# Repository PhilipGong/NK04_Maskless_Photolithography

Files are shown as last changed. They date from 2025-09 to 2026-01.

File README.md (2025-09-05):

# NK04_Maskless_Photolithography
Project repository for developing an LCOS based maskless photolithography process.

---
## Objective
To develope an optical setup which is able to:
- Achieve <= 1um feature size
- Ability to expose photoresists at wavelength (405nm / 465nm)
- (Optional) Step the substrate for wafer stepping
- (Optional) Make use of the phase-shift ability of LCOS for phase shift masking

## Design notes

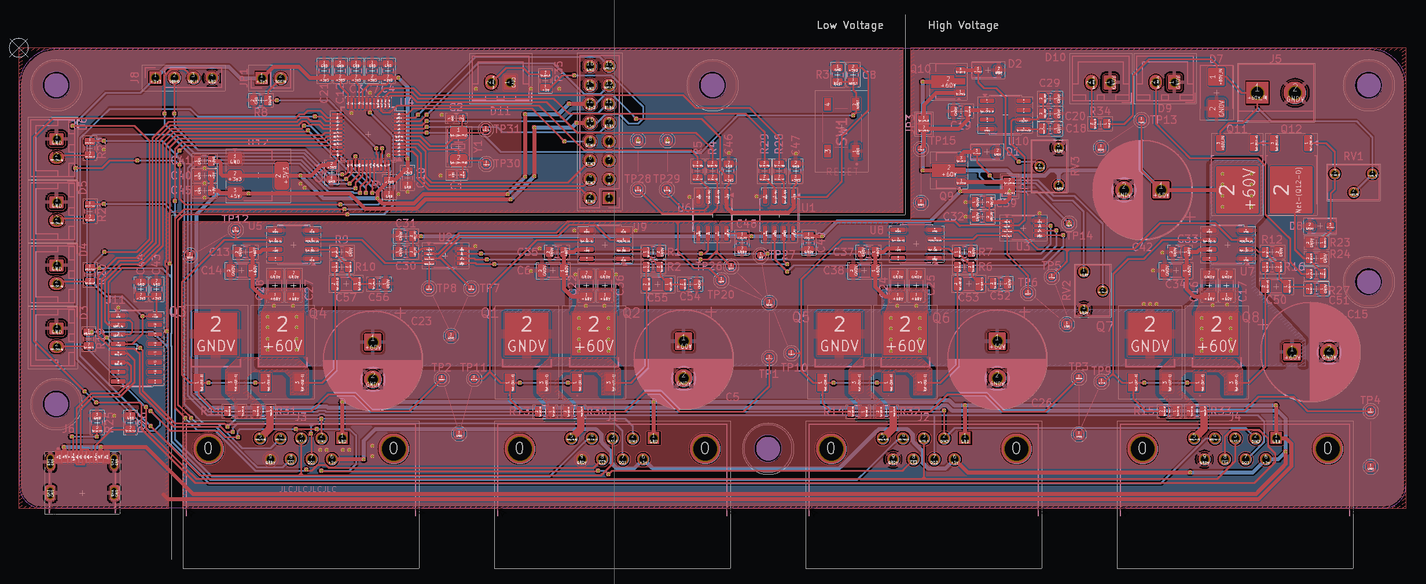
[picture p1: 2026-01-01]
Nanopositioner/Electronics/PCB_Screenshot.png

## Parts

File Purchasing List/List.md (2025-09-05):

## Objective
### Requirements:
- Magnification of 100x
- Numerical aperture of 0.95 or above
- Preferrably working in <400nm of light
### Possible candidates:
- TBD

---

## Photoresist
### Requirements:
- Ability to be exposed by 405nm / 435nm (g-line) / 365nm (i-line) of light
### Possible candidates:
- AZ703

---

## Movement stage
### Requirements:
- 3-axis / 5-axis
- Manual / Motorized (can be developed for autofocusing)
### Possible candidates:

- TBD

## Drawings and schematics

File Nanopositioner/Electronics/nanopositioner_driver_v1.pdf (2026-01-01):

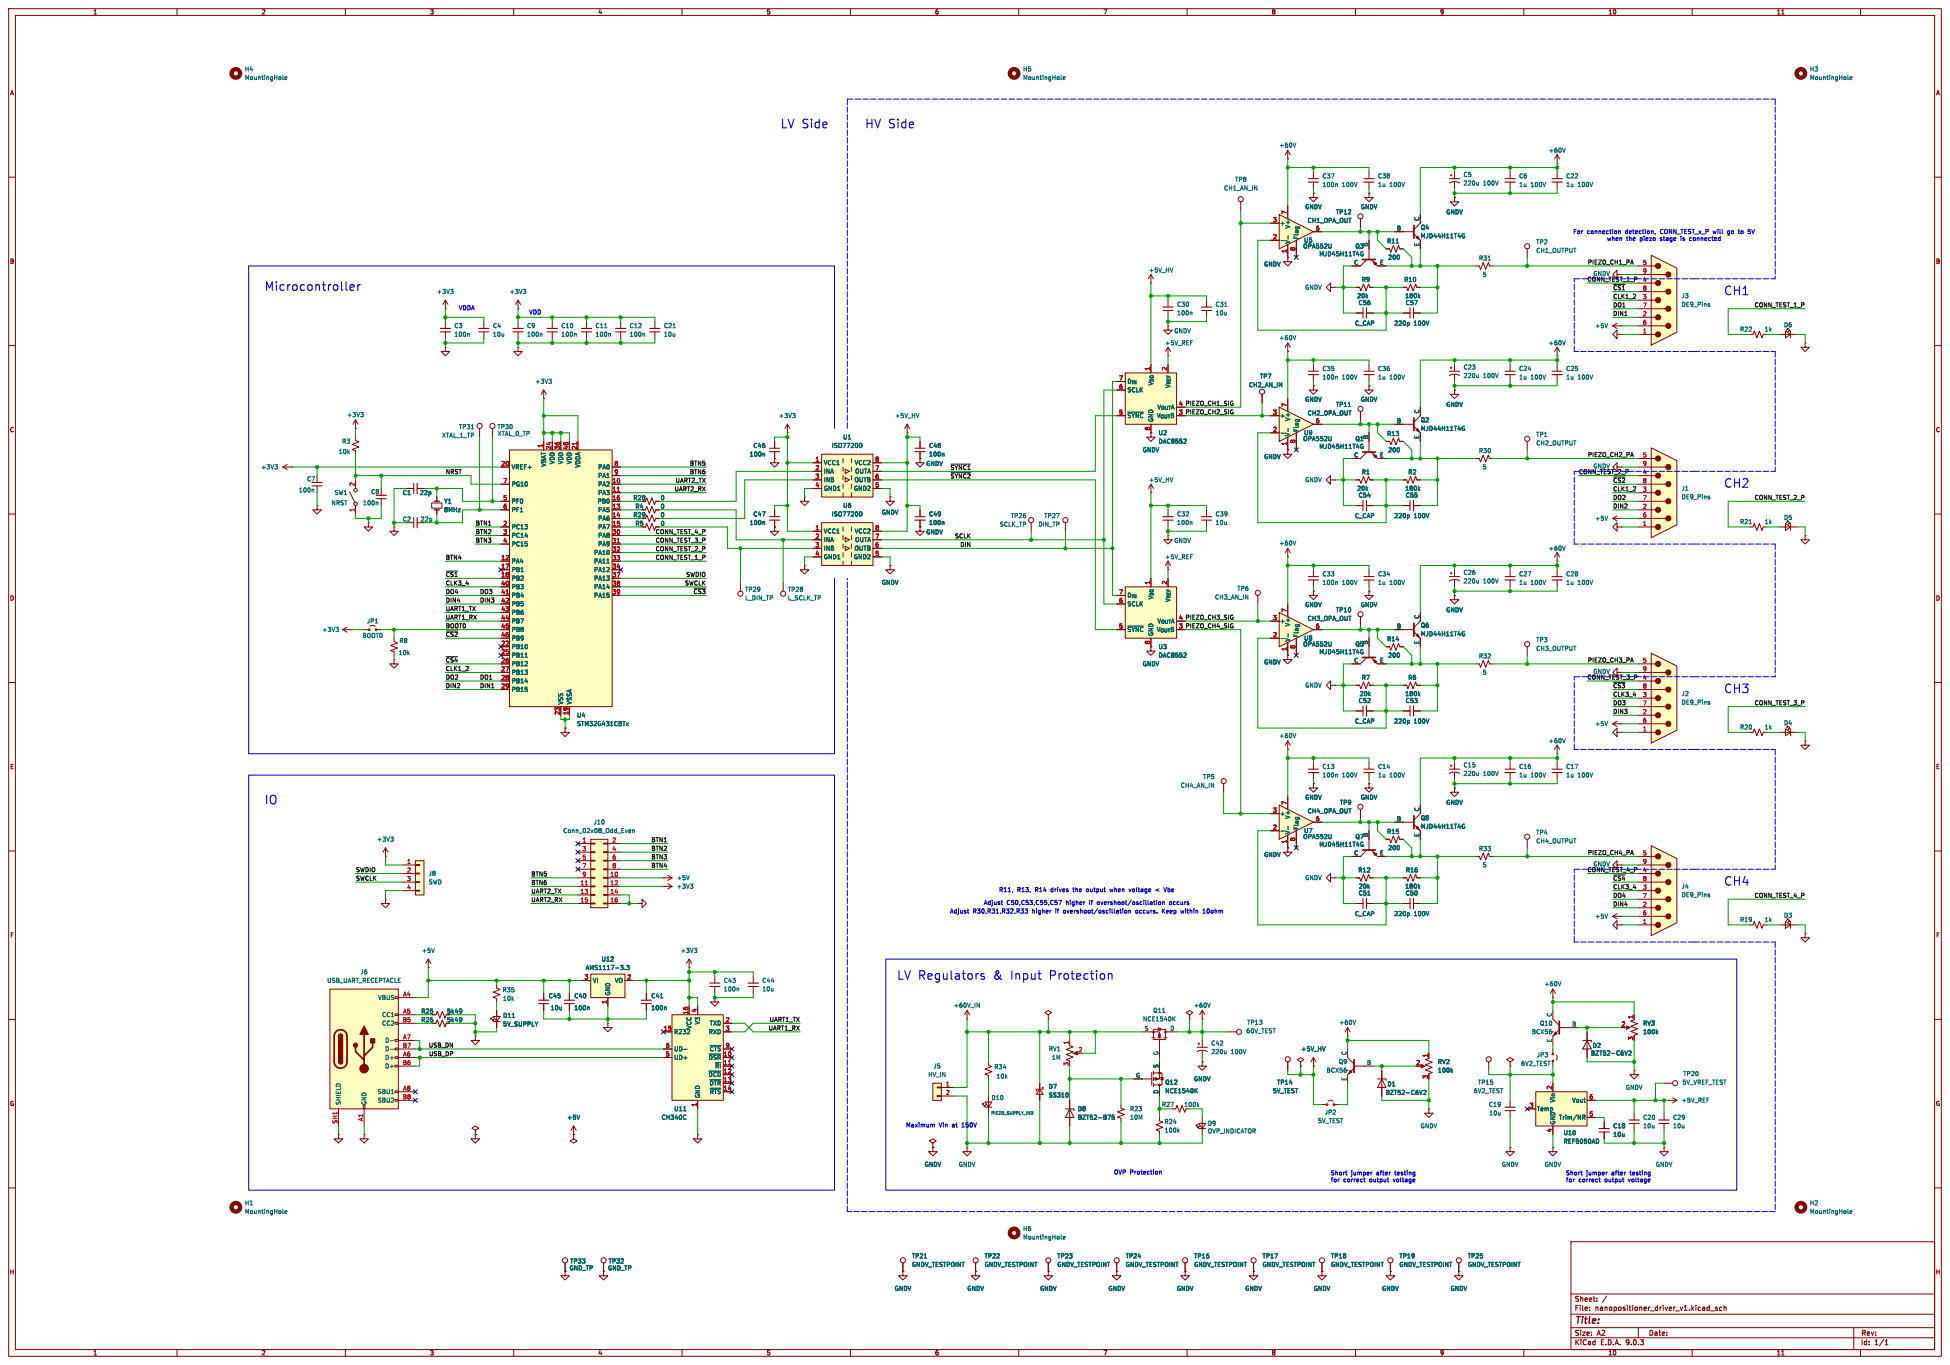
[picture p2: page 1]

1 VDD 24 VDD 36 VSS 23 VDD 48 VSSA 19 VDDA 21 PA0 8 PA1 9 PA2 10 PA3 11 PB0 16 PA5 13 PA6 14 PA7 15 PA8 30 PA9 31 PA10 32 PA11 33 PA12 34 PA13 37 PA14 38 PA15 39 Y1

1 VDD 24 VDD 36 VSS 23 VDD 48 VSSA 19 VDDA 21 PA0 8 PA1 9 PA2 10 PA3 11 PB0 16 PA5 13 PA6 14 PA7 15 PA8 30 PA9 31 PA10 32 PA11 33 PA12 34 PA13 37 PA14 38 PA15 39 U4STM32G431CBTx

1 TXD 2 RXD 3 ~{CTS}9 ~{DSR} 10 ~{RI} 11 ~{DCD} 12 ~{DTR} 13 ~{RTS} 14 D11

1 TXD 2 RXD 3 ~{CTS}9 ~{DSR} 10 ~{RI} 11 ~{DCD} 12 ~{DTR} 13 ~{RTS} 14 U11 CH340C

GNDV
Short jumper after testing
for correct output voltage

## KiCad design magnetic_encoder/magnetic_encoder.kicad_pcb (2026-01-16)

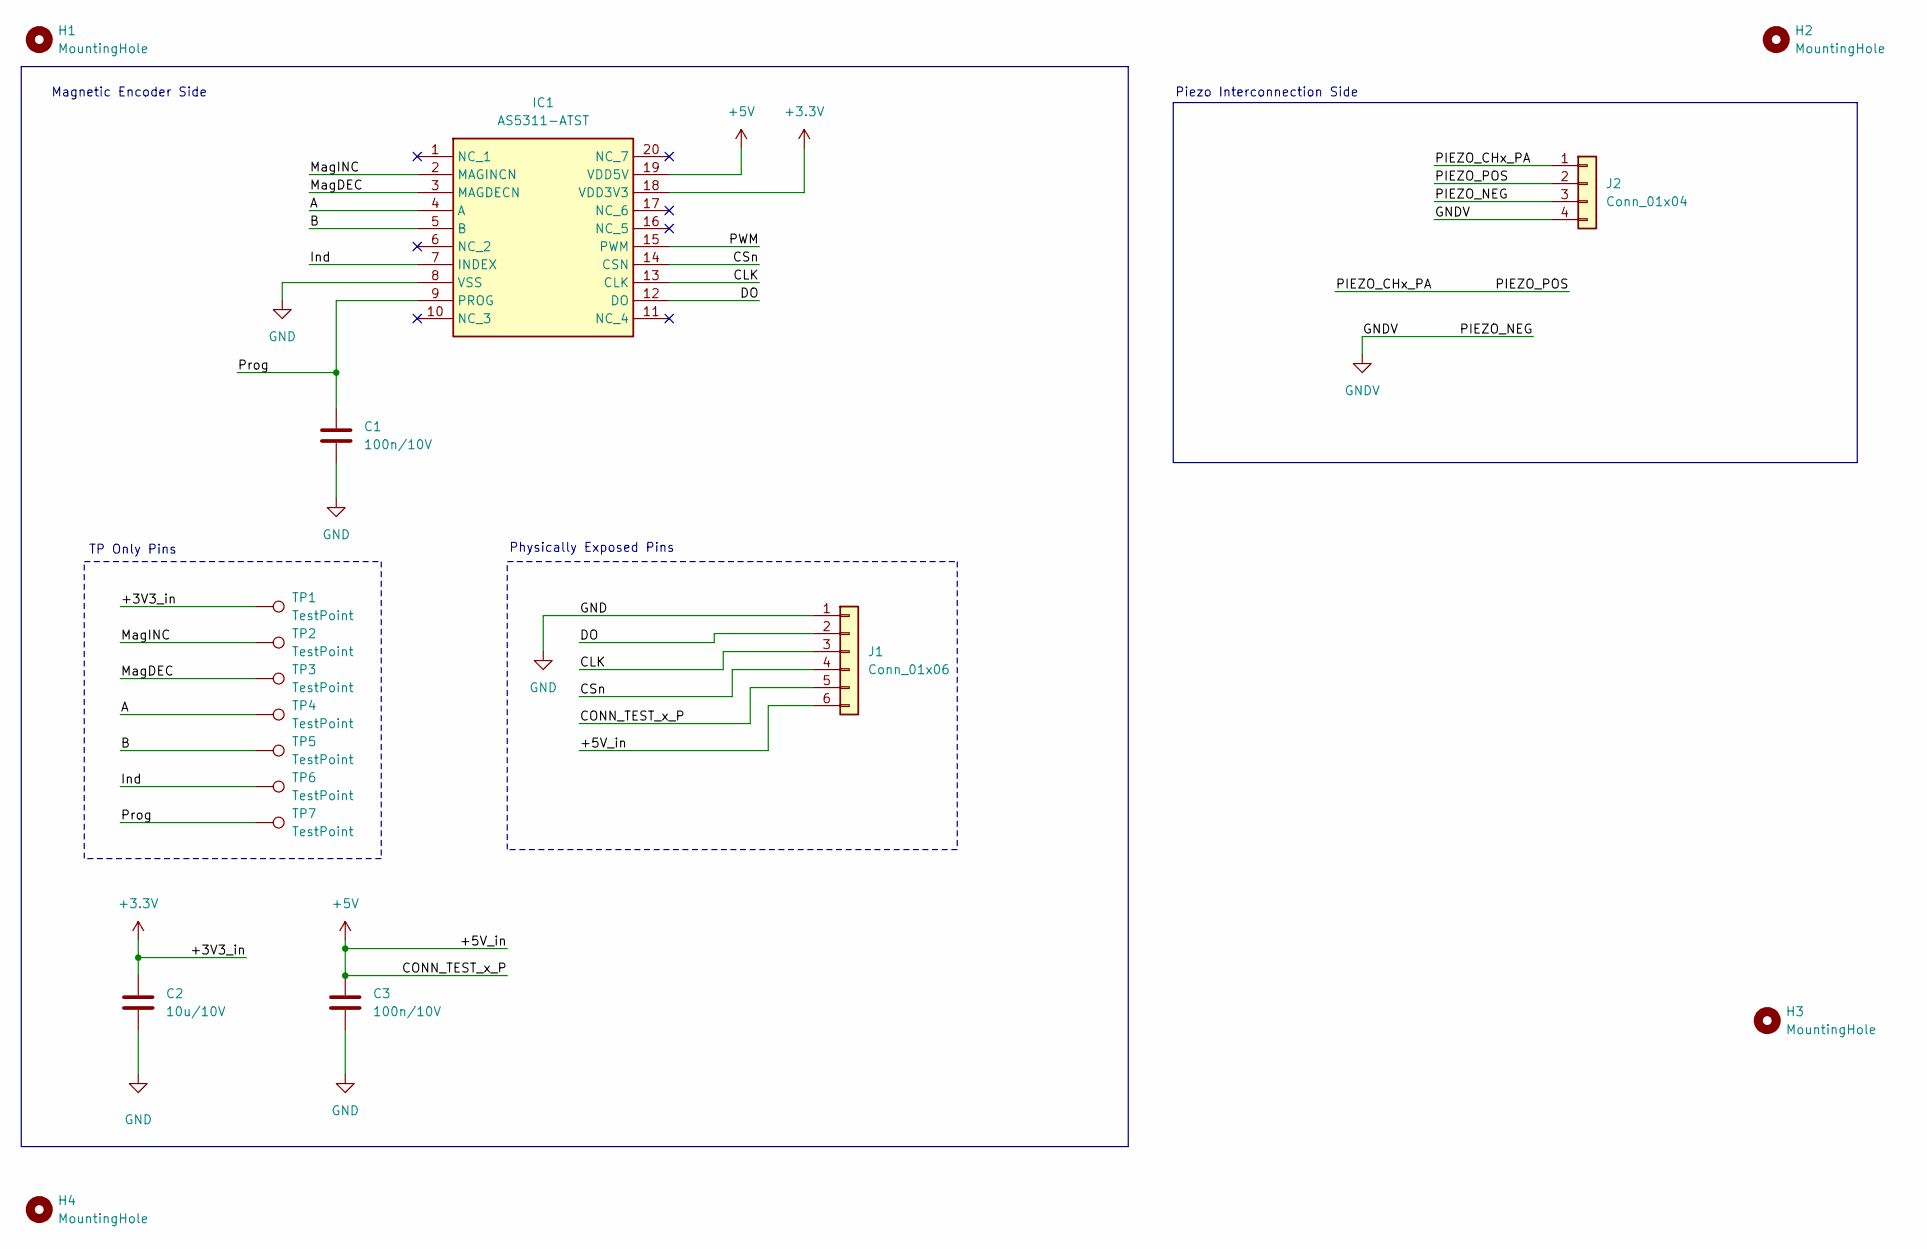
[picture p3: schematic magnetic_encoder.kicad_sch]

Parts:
C1, C3: 100n/10V; C_0805_2012Metric
C2: 10u/10V; C_0805_2012Metric
H1, H2, H3, H4: MountingHole; MountingHole_3.2mm_M3
IC1: AS5311-ATST; SOP65P640X120-20N; Manufacturer_Part_Number AS5311-ATST; Mouser Part Number 985-AS5311-ATST
J1: Conn_01x06; SolderWire-0.5sqmm_1x06_P4.6mm_D0.9mm_OD2.1mm_Relief
J2: Conn_01x04; SolderWire-0.5sqmm_1x04_P4.6mm_D0.9mm_OD2.1mm_Relief
TP1, TP2, TP3, TP4, TP5, TP6, TP7: TestPoint; TestPoint_Pad_D1.0mm

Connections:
+3.3V: C2.1, IC1.18 (VDD3V3), TP1.1
+5V: C3.1, IC1.19 (VDD5V), J1.5, J1.6
/A: IC1.4 (A), TP4.1
/B: IC1.5 (B), TP5.1
/CLK: IC1.13 (CLK), J1.3
/CSn: IC1.14 (CSN), J1.4
/DO: IC1.12 (DO), J1.2
/Ind: IC1.7 (INDEX), TP6.1
/MagDEC: IC1.3 (MAGDECN), TP3.1
/MagINC: IC1.2 (MAGINCN), TP2.1
/PIEZO_CHx_PA: J2.1, J2.2
/PWM: IC1.15 (PWM)
/Prog: C1.1, IC1.9 (PROG), TP7.1
GND: C1.2, C2.2, C3.2, IC1.8 (VSS), J1.1
GNDV: J2.3, J2.4

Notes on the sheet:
Physically Exposed Pins
Piezo Interconnection Side
Magnetic Encoder Side
TP Only Pins

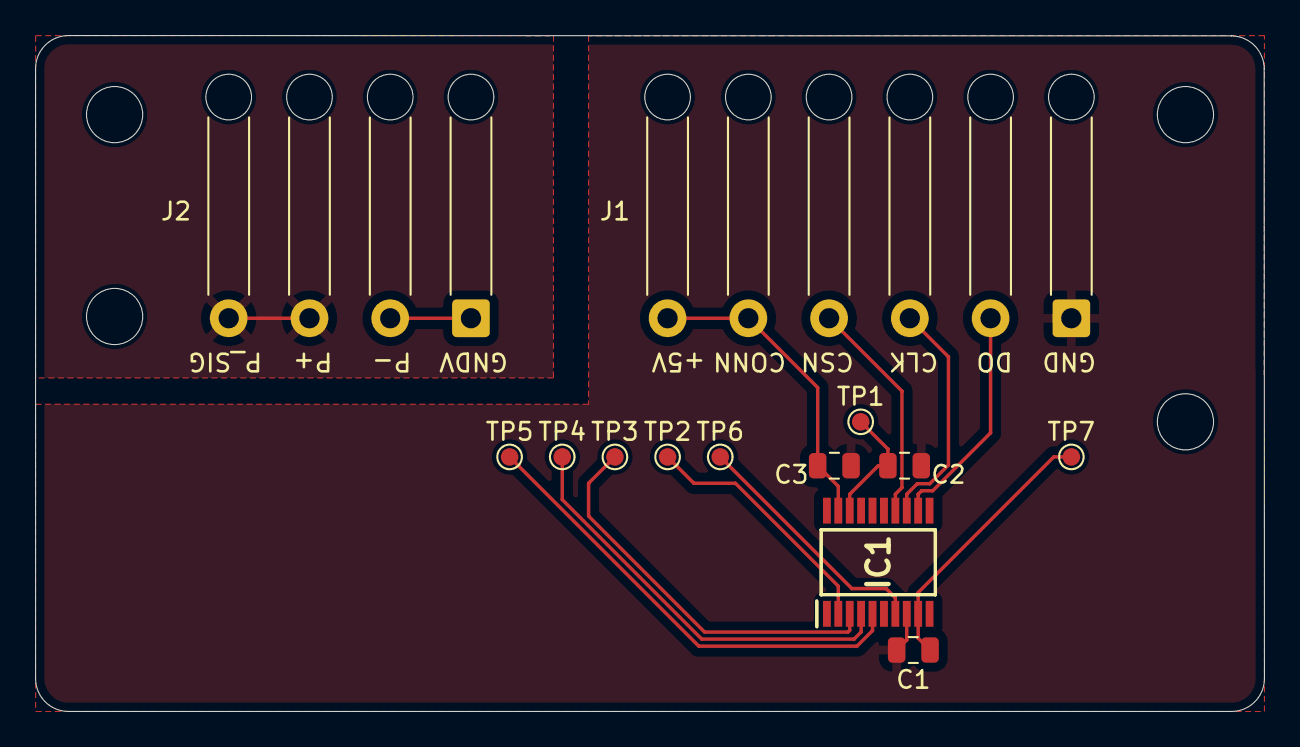
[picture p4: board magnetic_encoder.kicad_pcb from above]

Board: 2 copper layers, 70.0 x 38.5 mm, 17 parts (0 on the bottom side), 14 nets.

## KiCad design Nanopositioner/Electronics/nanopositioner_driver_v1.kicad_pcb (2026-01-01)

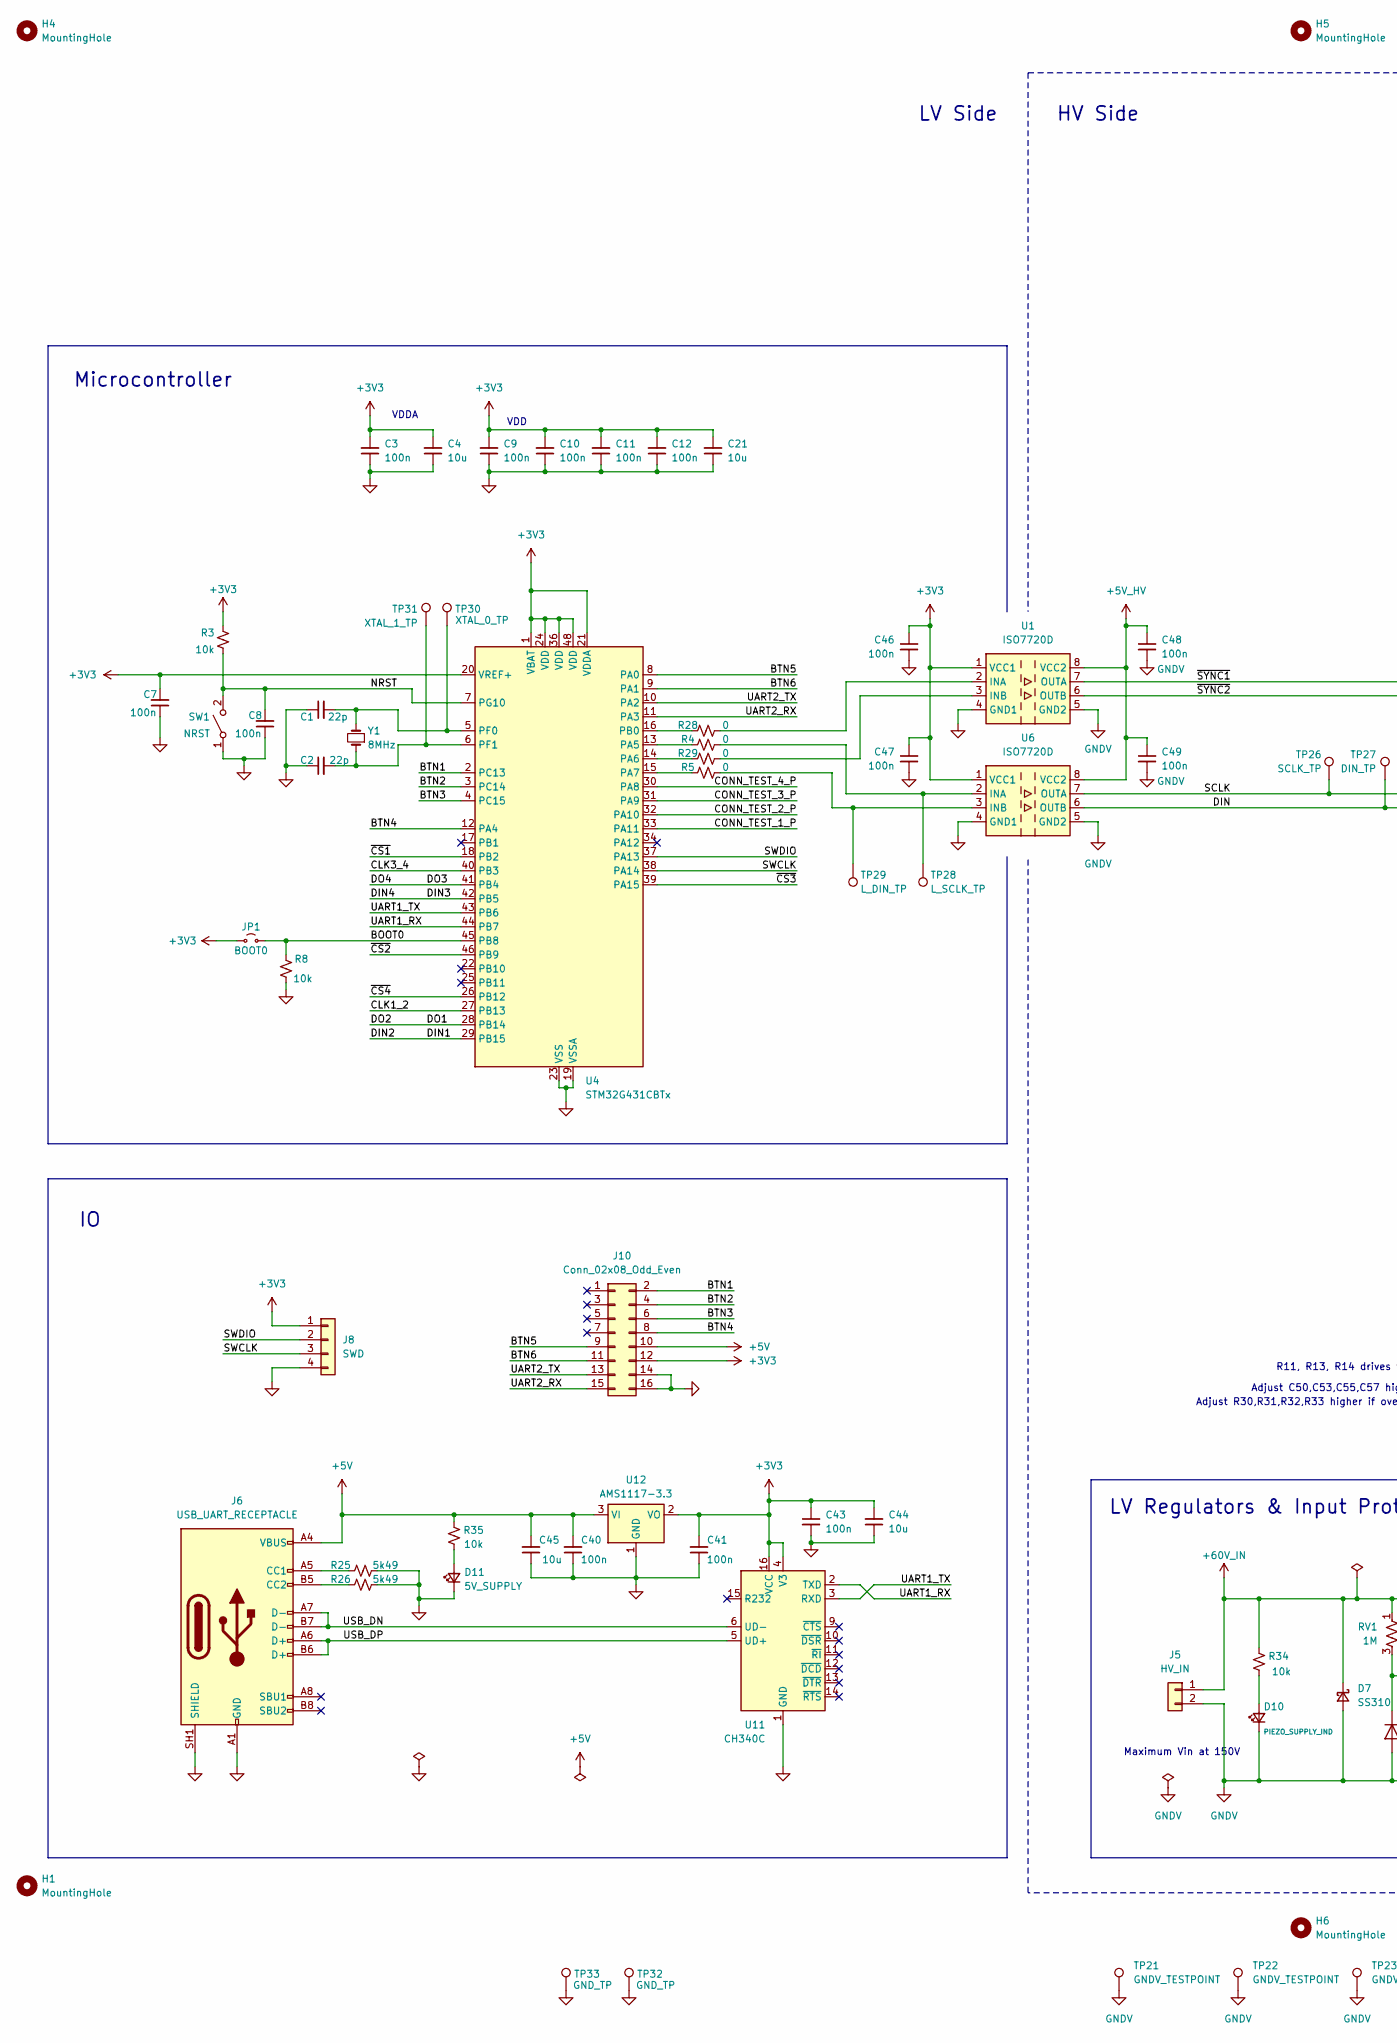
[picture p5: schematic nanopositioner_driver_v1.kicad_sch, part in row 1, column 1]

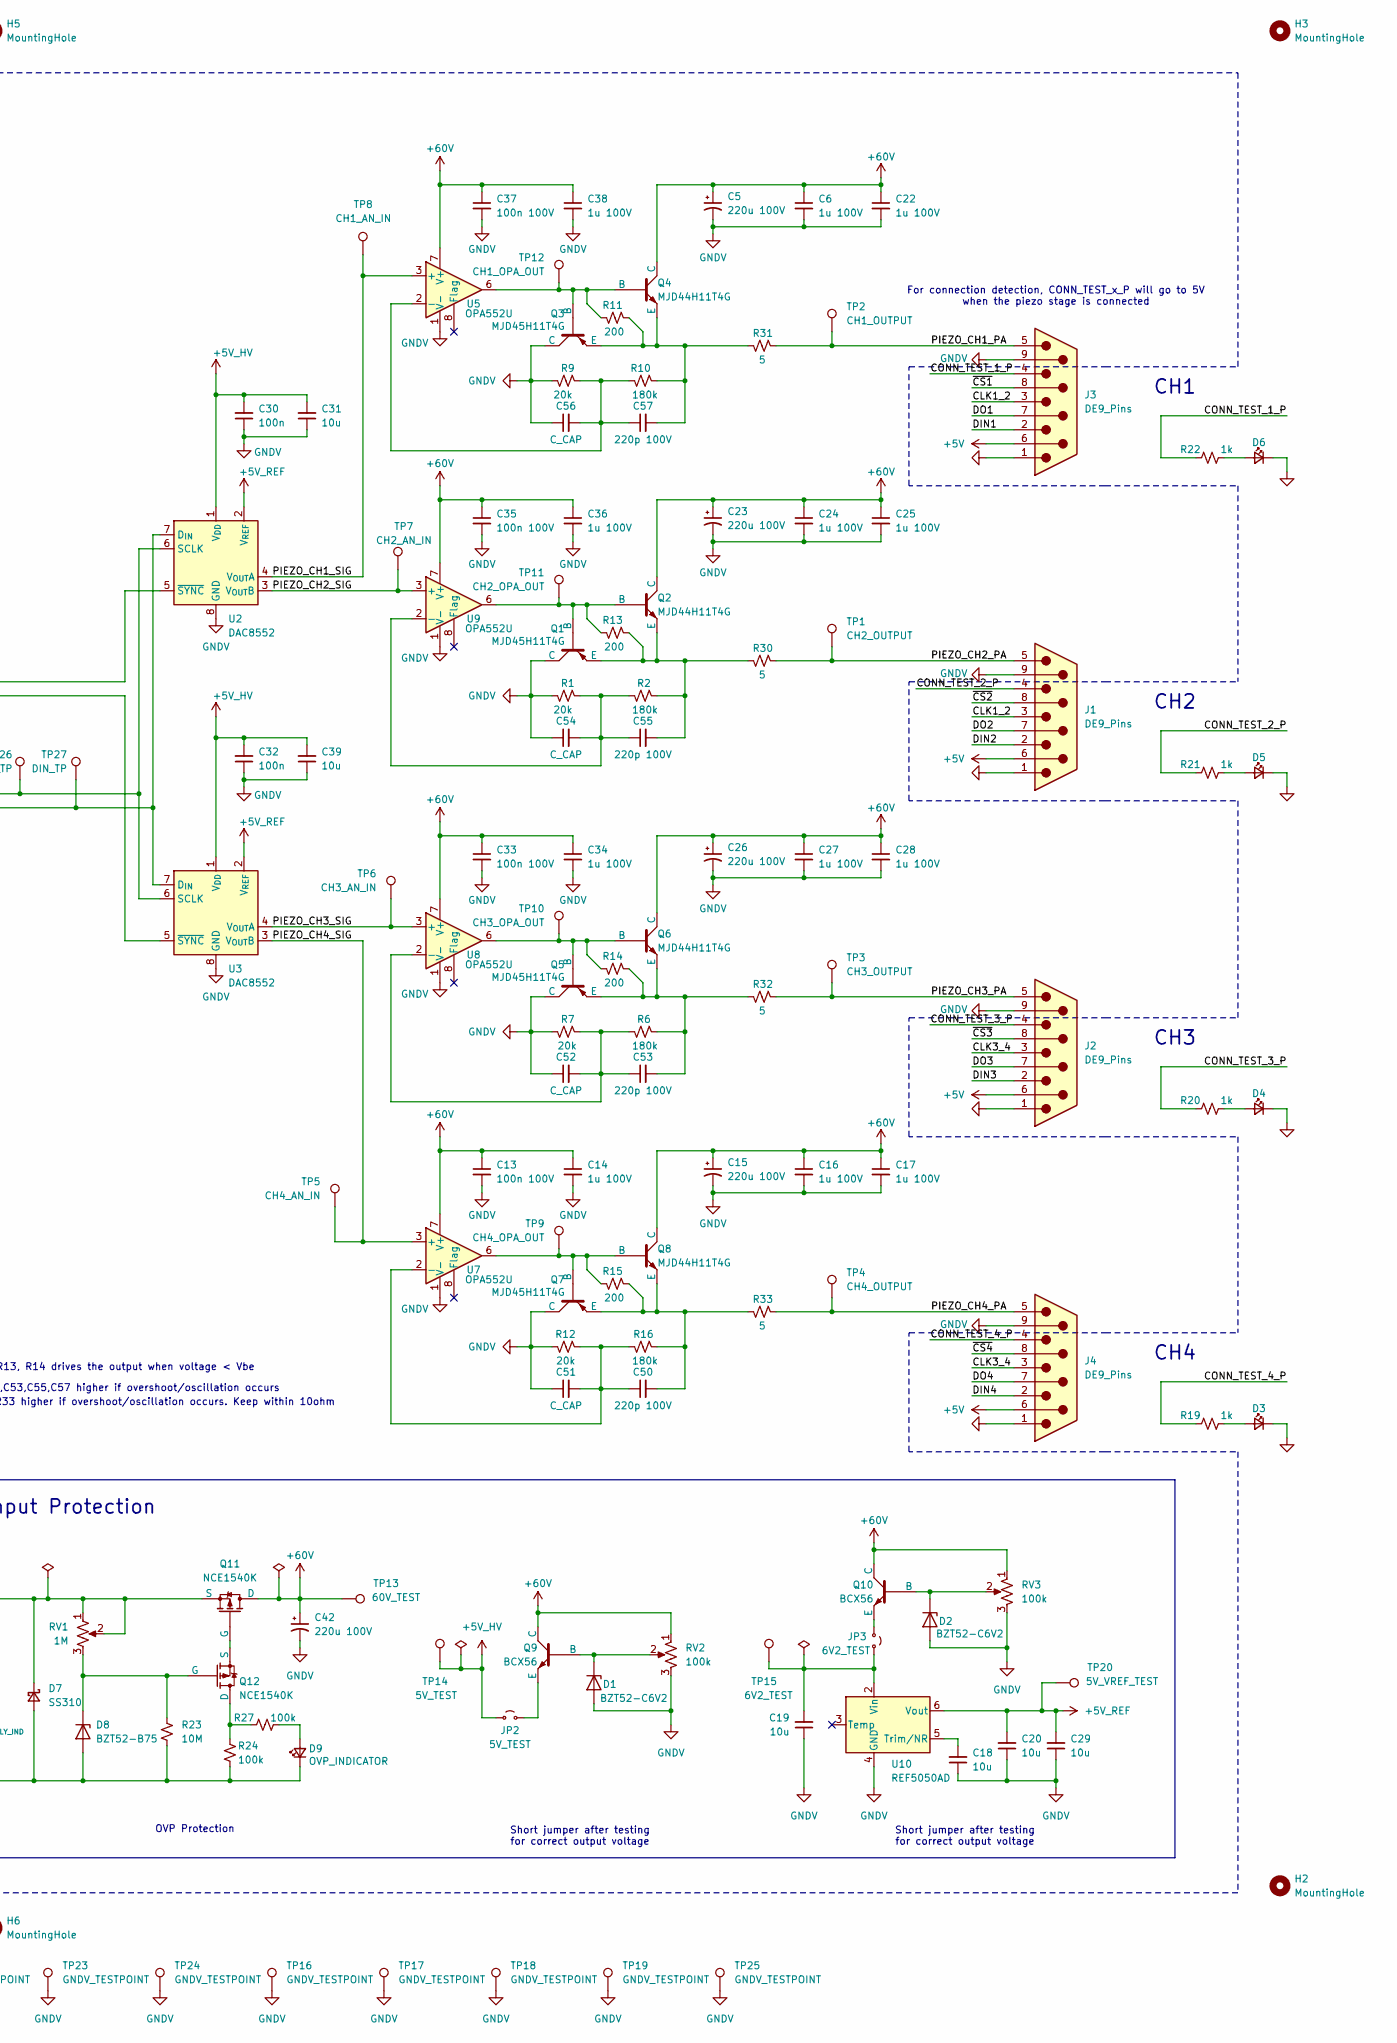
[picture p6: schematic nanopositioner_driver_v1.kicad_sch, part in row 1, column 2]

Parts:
C1, C2: 22p; C_0603_1608Metric
C3, C7, C8, C9, C10, C11, C12, C30, C32, C40, C41, C43, C46, C47, C48, C49: 100n; C_0805_2012Metric
C4, C18, C19, C20, C21, C29, C31, C39, C44, C45: 10u; C_0805_2012Metric
C5, C15, C23, C26, C42: 220u 100V; CP_Radial_D13.0mm_P5.00mm
C6, C14, C16, C17, C22, C24, C25, C27, C28, C34, C36, C38: 1u 100V; C_1206_3216Metric
C13, C33, C35, C37: 100n 100V; C_0805_2012Metric
C50, C53, C55, C57: 220p 100V; C_1206_3216Metric
C51, C52, C54, C56: C_CAP; C_0805_2012Metric
D1, D2: BZT52-C6V2; D_SOD-123F
D3, D4, D5, D6: LED_Small; JST_XH_B2B-XH-A_1x02_P2.50mm_Vertical
D7: SS310; D_SMB
D8: BZT52-B75; D_SOD-123F
D9: OVP_INDICATOR; JST_XH_B2B-XH-A_1x02_P2.50mm_Vertical
D10: PIEZO_SUPPLY_IND; JST_XH_B2B-XH-A_1x02_P2.50mm_Vertical
D11: 5V_SUPPLY; JST_XH_B2B-XH-A_1x02_P2.50mm_Vertical
H1, H2, H3, H4, H5, H6: MountingHole; MountingHole_3.2mm_M3
J1, J2, J3, J4: DE9_Pins; DSUB-9_Socket_Horizontal_P2.77x2.84mm_EdgePinOffset7.70mm_H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
J5: HV_IN; TerminalBlock_bornier-2_P5.08mm
J6: USB_UART_RECEPTACLE; GCT_USB4105GFA120
J8: SWD; PinSocket_1x04_P2.54mm_Vertical
J10: Conn_02x08_Odd_Even; PinHeader_2x08_P2.54mm_Vertical
JP1: BOOT0; PinHeader_1x02_P2.54mm_Vertical
JP2: 5V_TEST; SolderJumper-2_P1.3mm_Open_Pad1.0x1.5mm
JP3: 6V2_TEST; SolderJumper-2_P1.3mm_Open_Pad1.0x1.5mm
Q1, Q3, Q5, Q7: MJD45H11T4G; MJD45H11AJ
Q2, Q4, Q6, Q8: MJD44H11T4G; MJD44H11AJ
Q9, Q10: BCX56; SOT-89-3
Q11, Q12: NCE1540K; TO-252-2
R1, R7, R9, R12: 20k; R_0805_2012Metric
R2, R6, R10, R16: 180k; R_0805_2012Metric
R3, R8, R34, R35: 10k; R_0805_2012Metric
R4, R5, R28, R29: 0; R_0805_2012Metric
R11, R13, R14, R15: 200; R_0805_2012Metric
R19, R20, R21, R22: 1k; R_0805_2012Metric
R23: 10M; R_0805_2012Metric
R24, R27: 100k; R_0805_2012Metric
R25, R26: 5k49; R_0805_2012Metric
R30, R31, R32, R33: 5; R_0805_2012Metric
RV1: 1M; Potentiometer_Bourns_3266W_Vertical
RV2, RV3: 100k; Potentiometer_Bourns_3266W_Vertical
SW1: NRST; TL3342F260QG
TP1: CH2_OUTPUT; TestPoint_Pad_D1.0mm
TP2: CH1_OUTPUT; TestPoint_Pad_D1.0mm
TP3: CH3_OUTPUT; TestPoint_Pad_D1.0mm
TP4: CH4_OUTPUT; TestPoint_Pad_D1.0mm
TP5: CH4_AN_IN; TestPoint_Pad_D1.0mm
TP6: CH3_AN_IN; TestPoint_Pad_D1.0mm
TP7: CH2_AN_IN; TestPoint_Pad_D1.0mm
TP8: CH1_AN_IN; TestPoint_Pad_D1.0mm
TP9: CH4_OPA_OUT; TestPoint_Pad_D1.0mm
TP10: CH3_OPA_OUT; TestPoint_Pad_D1.0mm
TP11: CH2_OPA_OUT; TestPoint_Pad_D1.0mm
TP12: CH1_OPA_OUT; TestPoint_Pad_D1.0mm
TP13: 60V_TEST; TestPoint_Pad_D1.0mm
TP14: 5V_TEST; TestPoint_Pad_D1.0mm
TP15: 6V2_TEST; TestPoint_Pad_D1.0mm
TP16, TP17, TP18, TP19, TP21, TP22, TP23, TP24, TP25: GNDV_TESTPOINT; TestPoint_Pad_D1.0mm
TP20: 5V_VREF_TEST; TestPoint_Pad_D1.0mm
TP26: SCLK_TP; TestPoint_Pad_D1.0mm
TP27: DIN_TP; TestPoint_Pad_D1.0mm
TP28: L_SCLK_TP; TestPoint_Pad_D1.0mm
TP29: L_DIN_TP; TestPoint_Pad_D1.0mm
TP30: XTAL_0_TP; TestPoint_Pad_D1.0mm
TP31: XTAL_1_TP; TestPoint_Pad_D1.0mm
TP32, TP33: GND_TP; TestPoint_Pad_D1.0mm
U1, U6: ISO7720D; SOIC-8_3.9x4.9mm_P1.27mm
U2, U3: DAC8552; Texas_S-PDSO-G8_3x3mm_P0.65mm
U4: STM32G431CBTx; LQFP-48_7x7mm_P0.5mm
U5, U7, U8, U9: OPA552U; SOIC-8_3.9x4.9mm_P1.27mm
U10: REF5050AD; SOIC-8_3.9x4.9mm_P1.27mm
U11: CH340C; SOIC-16_3.9x9.9mm_P1.27mm
U12: AMS1117-3.3; SOT-223-3_TabPin2
Y1: 8MHz; YSX530

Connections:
+3V3: C3.2, C4.2, C7.2, C9.2, C10.2, C11.2, C12.2, C21.2, C41.2, C43.1, C44.2, C46.1, C47.1, J8.1, J10.12, JP1.1 (A), R3.2, U1.1 (VCC1), U4.1 (VBAT), U4.20 (VREF+), U4.21 (VDDA), U4.24 (VDD), U4.36 (VDD), U4.48 (VDD), U6.1 (VCC1), U11.4 (V3), U11.16 (VCC), U12.2 (VO)
+5V: C40.2, C45.2, J1.6, J2.6, J3.6, J4.6, J6.A4 (VBUS), J6.A9 (VBUS), J6.B4 (VBUS), J6.B9 (VBUS), J10.10, R35.1, U12.3 (VI)
+5V_HV: C30.2, C31.2, C32.2, C39.2, C48.1, C49.1, JP2.1 (A), TP14.1, U1.8 (VCC2), U2.1 (V_{DD}), U3.1 (V_{DD}), U6.8 (VCC2)
+5V_REF: C20.2, C29.2, TP20.1, U2.2 (V_{REF}), U3.2 (V_{REF}), U10.6 (Vout)
+60V: C5.1, C6.1, C13.1, C14.1, C15.1, C16.1, C17.1, C22.1, C23.1, C24.1, C25.1, C26.1, C27.1, C28.1, C33.1, C34.1, C35.1, C36.1, C37.1, C38.1, C42.1, Q2.2 (C), Q4.2 (C), Q6.2 (C), Q8.2 (C), Q9.2 (C), Q10.2 (C), Q11.2 (D), RV2.1, RV3.1, TP13.1, U5.7 (V+), U7.7 (V+), U8.7 (V+), U9.7 (V+)
+60V_IN: D7.1 (K), J5.1, Q11.3 (S), R34.1, RV1.1, RV1.2
/BOOT0: JP1.2 (B), R8.1, U4.45 (PB8)
/BTN1: J10.2, U4.2 (PC13)
/BTN2: J10.4, U4.3 (PC14)
/BTN3: J10.6, U4.4 (PC15)
/BTN4: J10.8, U4.12 (PA4)
/BTN5: J10.9, U4.8 (PA0)
/BTN6: J10.11, U4.9 (PA1)
/CLK1_2: J1.3, J3.3, U4.27 (PB13)
/CLK3_4: J2.3, J4.3, U4.40 (PB3)
/CONN_TEST_1_P: J3.4, R22.1, U4.33 (PA11)
/CONN_TEST_2_P: J1.4, R21.1, U4.32 (PA10)
/CONN_TEST_3_P: J2.4, R20.1, U4.31 (PA9)
/CONN_TEST_4_P: J4.4, R19.1, U4.30 (PA8)
/DIN: TP27.1, U2.7 (D_{IN}), U3.7 (D_{IN}), U6.6 (OUTB)
/DIN1: J1.2, J3.2, U4.29 (PB15)
/DIN3: J2.2, J4.2, U4.42 (PB5)
/DO1: J1.7, J3.7, U4.28 (PB14)
/DO3: J2.7, J4.7, U4.41 (PB4)
/NRST: C8.2, R3.1, SW1.2 (B), U4.7 (PG10)
/PIEZO_CH1_PA: J3.5, R31.1, TP2.1
/PIEZO_CH1_SIG: TP8.1, U2.4 (V_{OUT}A), U5.3 (+)
/PIEZO_CH2_PA: J1.5, R30.1, TP1.1
/PIEZO_CH2_SIG: TP7.1, U2.3 (V_{OUT}B), U9.3 (+)
/PIEZO_CH3_PA: J2.5, R32.1, TP3.1
/PIEZO_CH3_SIG: TP6.1, U3.4 (V_{OUT}A), U8.3 (+)
/PIEZO_CH4_PA: J4.5, R33.1, TP4.1
/PIEZO_CH4_SIG: TP5.1, U3.3 (V_{OUT}B), U7.3 (+)
/SCLK: TP26.1, U2.6 (SCLK), U3.6 (SCLK), U6.7 (OUTA)
/SWCLK: J8.3, U4.38 (PA14)
/SWDIO: J8.2, U4.37 (PA13)
/UART1_RX: U4.44 (PB7), U11.2 (TXD)
/UART1_TX: U4.43 (PB6), U11.3 (RXD)
/UART2_RX: J10.15, U4.11 (PA3)
/UART2_TX: J10.13, U4.10 (PA2)
/USB_DN: J6.A7 (D-), J6.B7 (D-), U11.6 (UD-)
/USB_DP: J6.A6 (D+), J6.B6 (D+), U11.5 (UD+)
/~CS1: J3.8, U4.18 (PB2)
/~CS2: J1.8, U4.46 (PB9)
/~CS3: J2.8, U4.39 (PA15)
/~CS4: J4.8, U4.26 (PB12)
/~SYNC1: U1.7 (OUTA), U2.5 (~SYNC)
/~SYNC2: U1.6 (OUTB), U3.5 (~SYNC)
GND: C1.1, C2.1, C3.1, C4.1, C7.1, C8.1, C9.1, C10.1, C11.1, C12.1, C21.1, C40.1, C41.1, C43.2, C44.1, C45.1, C46.2, C47.2, D3.1 (K), D4.1 (K), D5.1 (K), D6.1 (K), D11.1 (K), J1.1, J2.1, J3.1, J4.1, J6.A1 (GND), J6.A12 (GND), J6.B1 (GND), J6.B12 (GND), J6.SH1 (SHIELD), J6.SH2 (SHIELD), J6.SH3 (SHIELD), J6.SH4 (SHIELD), J8.4, J10.14, J10.16, R8.2, R25.1, R26.1, SW1.1 (A), TP32.1, TP33.1, U1.4 (GND1), U4.19 (VSSA), U4.23 (VSS), U4.35 (VSS), U4.47 (VSS), U6.4 (GND1), U11.1 (GND), U12.1 (GND)
GNDV: C5.2, C6.2, C13.2, C14.2, C15.2, C16.2, C17.2, C18.1, C19.1, C20.1, C22.2, C23.2, C24.2, C25.2, C26.2, C27.2, C28.2, C29.1, C30.1, C31.1, C32.1, C33.2, C34.2, C35.2, C36.2, C37.2, C38.2, C39.1, C42.2, C48.2, C49.2, C51.1, C52.1, C54.1, C56.1, D1.2 (A), D2.2 (A), D7.2 (A), D8.2 (A), D9.1 (K), D10.1 (K), J1.9, J2.9, J3.9, J4.9, J5.2, Q1.2 (C), Q3.2 (C), Q5.2 (C), Q7.2 (C), R1.2, R7.2, R9.2, R12.2, R23.2, R24.1, RV2.3, RV3.3, TP16.1, TP17.1, TP18.1, TP19.1, TP21.1, TP22.1, TP23.1, TP24.1, TP25.1, U1.5 (GND2), U2.8 (GND), U3.8 (GND), U5.1 (V-), U5.4 (V-), U5.5 (V-), U6.5 (GND2), U7.1 (V-), U7.4 (V-), U7.5 (V-), U8.1 (V-), U8.4 (V-), U8.5 (V-), U9.1 (V-), U9.4 (V-), U9.5 (V-), U10.4 (GND)
unnamed: D1.1 (K), Q9.3 (B), RV2.2
unnamed: D2.1 (K), Q10.3 (B), RV3.2
unnamed: D3.2 (A), R19.2
unnamed: D4.2 (A), R20.2
unnamed: D5.2 (A), R21.2
unnamed: D6.2 (A), R22.2
unnamed: D8.1 (K), Q12.1 (G), R23.1, RV1.3
unnamed: D9.2 (A), R27.1
unnamed: D10.2 (A), R34.2
unnamed: D11.2 (A), R35.2
unnamed: J6.A5 (CC1), R25.2
unnamed: J6.B5 (CC2), R26.2
unnamed: JP2.2 (B), Q9.1 (E)
unnamed: JP3.1 (A), Q10.1 (E)
unnamed: C19.2, JP3.2 (B), TP15.1, U10.2 (Vin)
unnamed: Q1.1 (B), Q2.1 (B), R13.2, TP11.1, U9.6
unnamed: C55.2, Q1.3 (E), Q2.3 (E), R2.1, R13.1, R30.2
unnamed: Q3.1 (B), Q4.1 (B), R11.2, TP12.1, U5.6
unnamed: C57.2, Q3.3 (E), Q4.3 (E), R10.1, R11.1, R31.2
unnamed: Q5.1 (B), Q6.1 (B), R14.2, TP10.1, U8.6
unnamed: C53.2, Q5.3 (E), Q6.3 (E), R6.1, R14.1, R32.2
unnamed: Q7.1 (B), Q8.1 (B), R15.2, TP9.1, U7.6
unnamed: C50.2, Q7.3 (E), Q8.3 (E), R15.1, R16.1, R33.2
unnamed: Q11.1 (G), Q12.3 (S)
unnamed: Q12.2 (D), R24.2, R27.2
unnamed: R28.2, U1.2 (INA)
unnamed: R29.2, U1.3 (INB)
unnamed: R4.1, U4.13 (PA5)
unnamed: R29.1, U4.14 (PA6)
unnamed: R5.1, U4.15 (PA7)
unnamed: R28.1, U4.16 (PB0)
unnamed: C1.2, TP30.1, U4.5 (PF0), Y1.2
unnamed: C2.2, TP31.1, U4.6 (PF1), Y1.1
unnamed: C56.2, C57.1, R9.1, R10.2, U5.2 (-)
unnamed: R4.2, TP28.1, U6.2 (INA)
unnamed: R5.2, TP29.1, U6.3 (INB)
unnamed: C50.1, C51.2, R12.1, R16.2, U7.2 (-)
unnamed: C52.2, C53.1, R6.2, R7.1, U8.2 (-)
unnamed: C54.2, C55.1, R1.1, R2.2, U9.2 (-)
unnamed: C18.2, U10.5 (Trim/NR)

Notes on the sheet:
Short jumper after testing for correct output voltage
OVP Protection
CH1
HV Side
LV Regulators & Input Protection
Adjust C50,C53,C55,C57 higher if overshoot/oscillation occurs
VDDA
Microcontroller
VDD
Maximum Vin at 150V
R11, R13, R14 drives the output when voltage < Vbe
CH3
CH2
LV Side
For connection detection, CONN_TEST_x_P will go to 5V when the piezo stage is connected
Adjust R30,R31,R32,R33 higher if overshoot/oscillation occurs. Keep within 10ohm
CH4

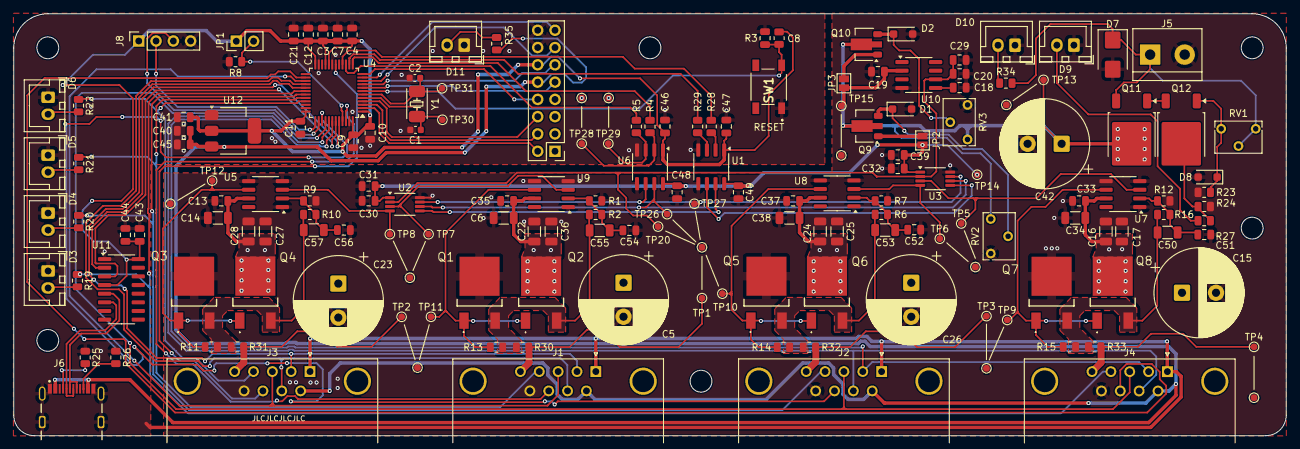
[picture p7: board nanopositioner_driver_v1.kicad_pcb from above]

Board: 2 copper layers, 187.0 x 62.0 mm, 180 parts (0 on the bottom side), 90 nets.

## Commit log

2025-11-14 Design of nanopositioner driver
    [nanopositioner_driver_v1.kicad_pcb, nanopositioner_driver_v1.kicad_sch]
2025-11-22 Updated the design of the mainboard
    [nanopositioner_driver_v1.kicad_sch]
2025-12-05 Updated driver design
    [nanopositioner_driver_v1.kicad_pcb, nanopositioner_driver_v1.kicad_sch]
2026-01-01 Updated the complete PCB design
    [nanopositioner_driver_v1.kicad_pcb, nanopositioner_driver_v1.kicad_sch]
2026-01-02 magnetic encoder sch+layout
    [magnetic_encoder.kicad_pcb, magnetic_encoder.kicad_sch]
2026-01-06 updated unused pins into testpoints
    [magnetic_encoder.kicad_pcb, magnetic_encoder.kicad_sch]
